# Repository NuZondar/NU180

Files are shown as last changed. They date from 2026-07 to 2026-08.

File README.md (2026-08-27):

# NU180
A reverse-engineered replacement for the U180 hybrid in the Hewlett-Packard / Agilent / Keysight 3458A DVM. 

Briefly, the custom "U180" hybrid in the 3458A is infamously prone to excessive drifting or outright failure, but is absolutely unavailable. NU180 is a drop-in replacement for that hybrid. Still under development, its performance falls slightly short of an original U180, e.g. noise performance is ~20-30% higher than spec, but it thus provides at least 8 digits conversion (within 2x of 8.5 digits), which is infinitely better than a dead or dying machine! 

Some notes:

The new Version 1.1 files are denoted "v11" in their names. 

The layout requires 6 layers. Choose a thin stack-up - that is, thinner core layers - if available. 

Choose the best resistors you can find, especially for their TCR (temperature coefficient of resistance). In particular, the use of low TCR bulk-foil resistors for at least the 50k and most-critical 80k's are recommended for best temperature stability. 

The footprints for the critical 80k's allow choosing either large 2512 surface-mount resistors, or else through-hole resistors (same for the 50k). These are intended for builders who are using bulk-foil resistors (80k's only come in 2512 size). You can edit the files to delete the unused footprints or else leave them in place. Another option for the 50k and 80k resistors is to edit the files to substitute a small array of series or parallel resistors. There's room for up to 4 each, e.g. 4x 20k in series for the 80k's, etc. 

You also have the option of using voltage regulation on the flip-flop and inverter (recommended), or else using unregulated 5V, chosen via jumpers. The schematic shows parts suitable for 3.3V operation, but other parts may allow operation down to 2.5V. The lower-voltage regulation should help keep noise down. 

The 100k resistors to ground are optional and need not be included unless some problem is seen. 

Debugging: The 3458A is a very sensitive instrument that can be quite fussy about error codes. At least in earlier versions, builders have sometimes found that changing the value of the series resistors (the 100 Ohm ones) up or down, e.g. to 33 or 220 Ohms, can help. Usually, only the four switch control lines associated with the 80k resistors (S5, S7, S9, S11) might need tuning. Another hack that has sometimes helped is adding a small capacitor (5-10 pF) in parallel with the R140 resistor on the A3 board.

There is extensive discussion of this project in the metrology section of EEVblog. Many people contributed their knowledge and experience towards its success, including MiDi, DB4UCH, wanghar, Kleinstein and others. 

Good luck!

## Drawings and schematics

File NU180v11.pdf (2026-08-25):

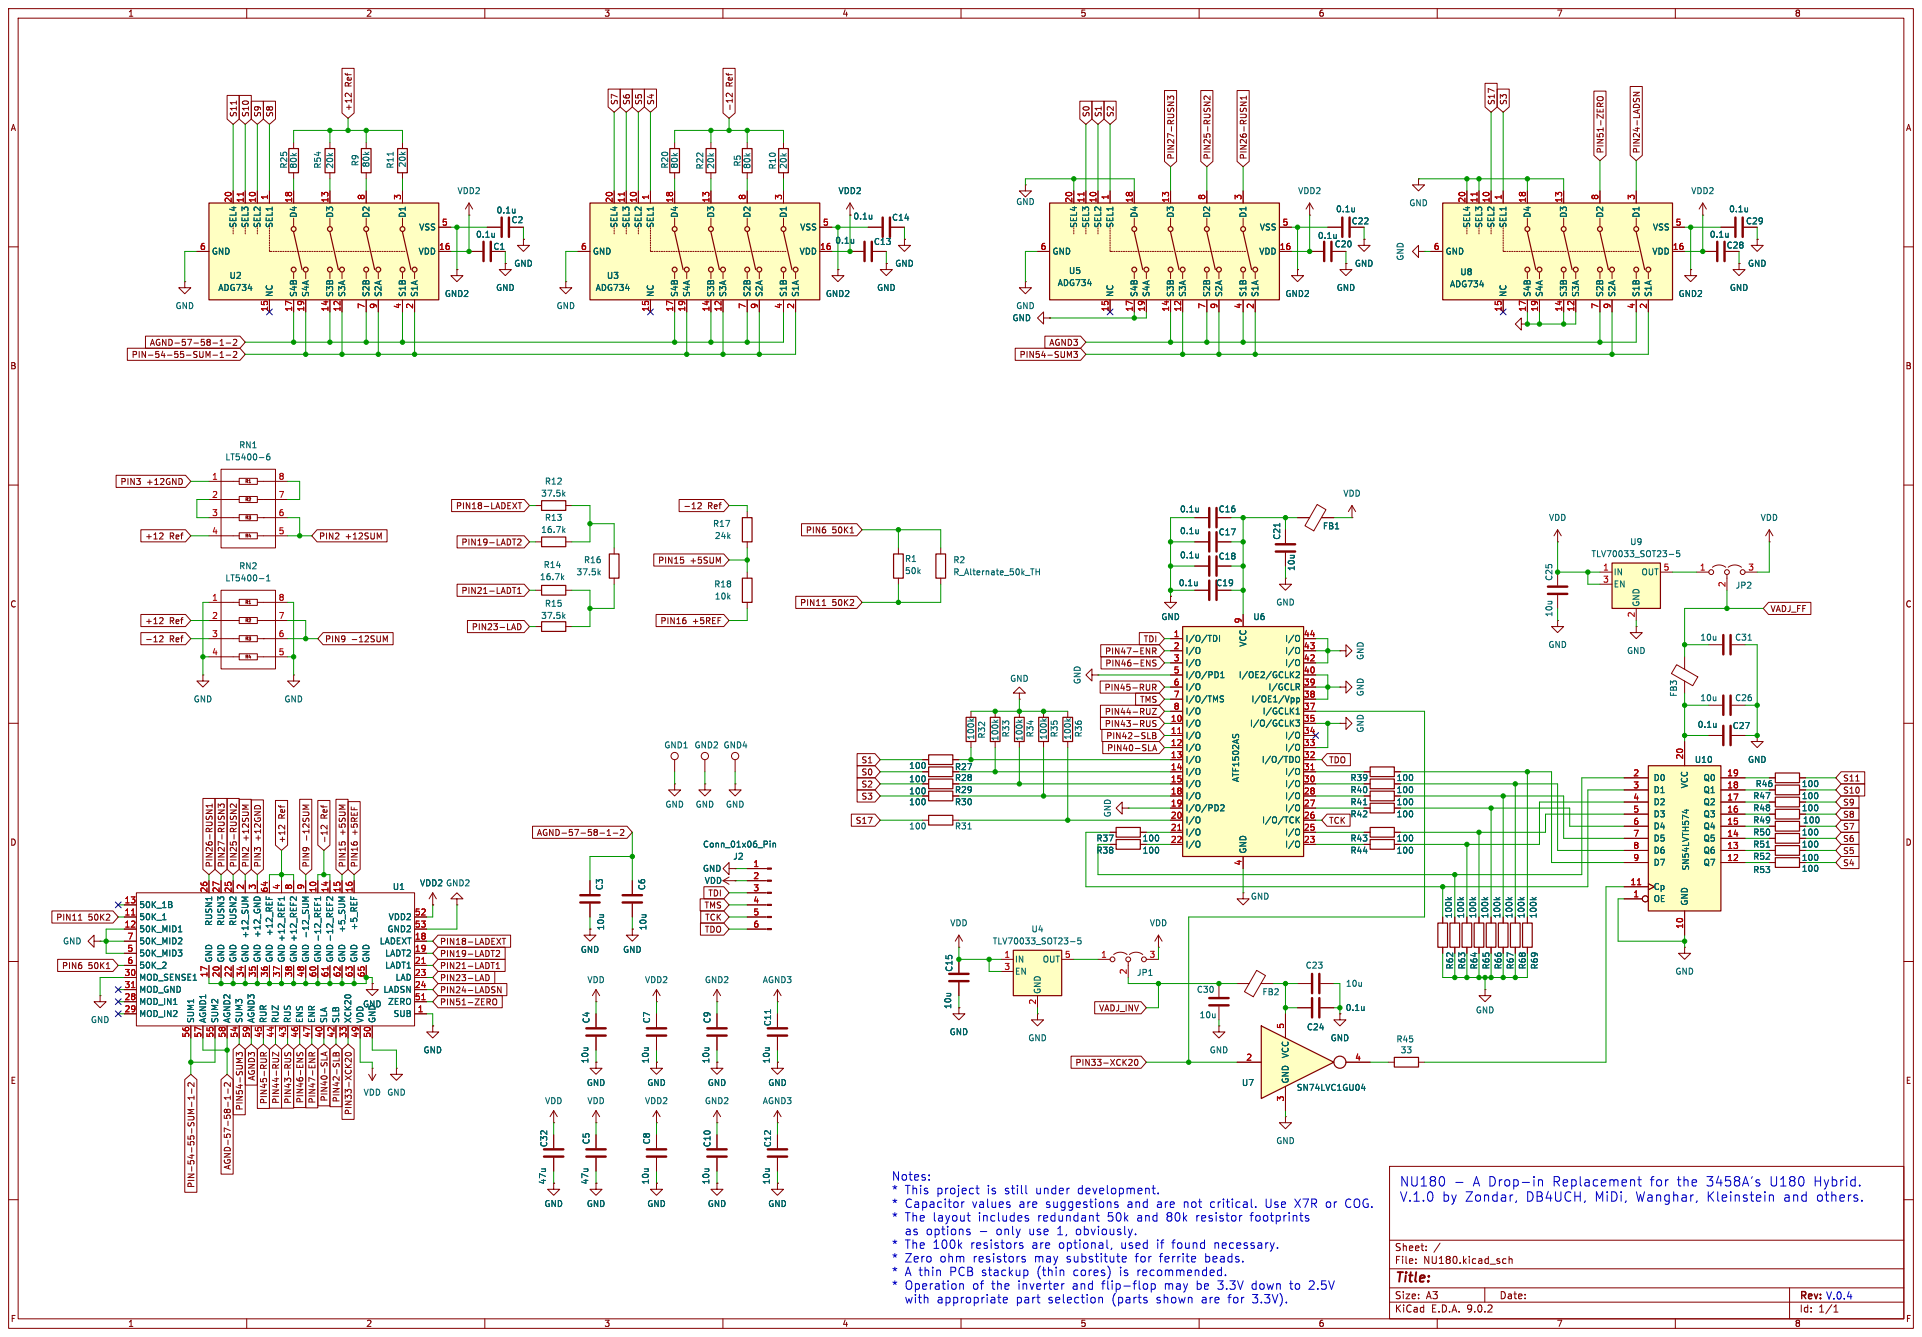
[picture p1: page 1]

2 OUT 5 U4 TLV70033_SOT23-5 GND GND2 GND GND C10 10u C6 10u GND

3 GND 35 RUR 45 +12_REF 64 GND 36 RUZ 44 +12_REF1

9 GND 48 ENR 47 -12_REF1 10 GND 60 SLA 40 -12_REF2 14 GND 61 SLB 42 +5_SUM 15 GND 62 XCK20 33 +5_REF 16 GND 63 VDD 49 GND 65 GND 50 VDD2 52 GND2 53

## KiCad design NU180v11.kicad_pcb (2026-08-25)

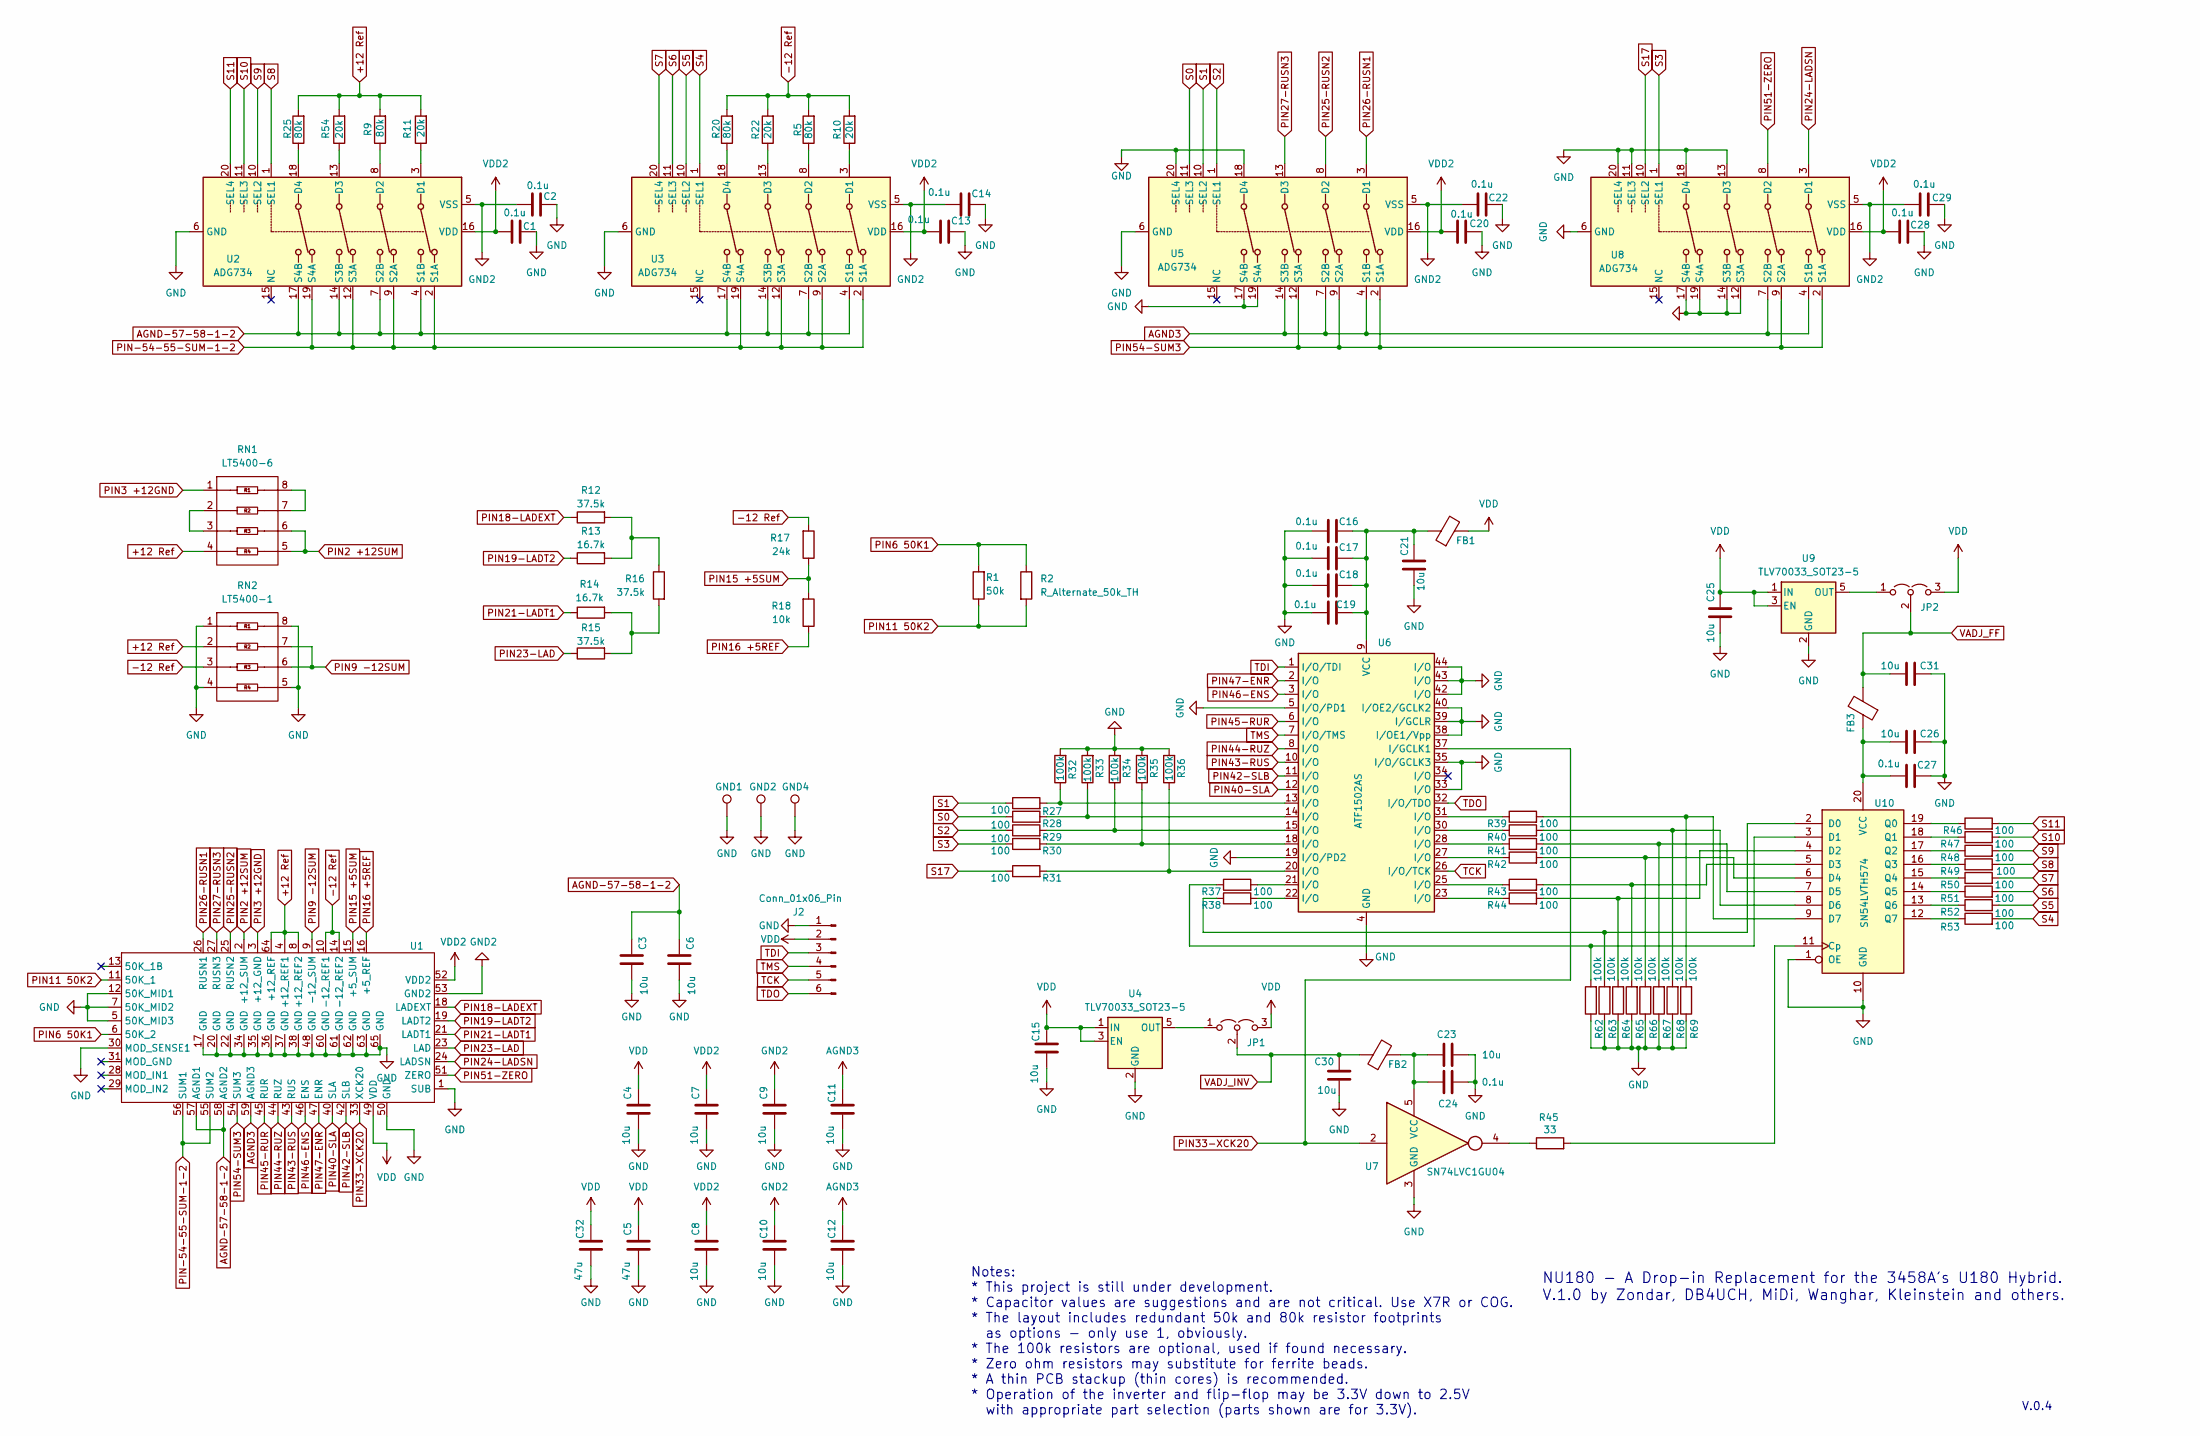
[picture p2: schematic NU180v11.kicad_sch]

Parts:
C1, C2, C13, C14, C16, C17, C18, C19, C20, C22, C24, C27, C28, C29: 0.1u; C_0603_1608Metric
C3, C4, C6, C7, C8, C9, C10, C11, C12, C15, C21, C23, C25, C26, C30, C31: 10u; C_0805_2012Metric_Pad1.18x1.45mm_HandSolder
C5, C32: 47u; C_1206_3216Metric
FB1, FB2, FB3: Ferrite Bead or Short; C_0603_1608Metric
GND1, GND2, GND4: TestPoint; PinHeader_1x01_P2.54mm_Vertical
J2: Conn_01x06_Pin; PinHeader_1x06_P2.54mm_Vertical
JP1, JP2: Jumper_3_Open; SolderJumper-3_P2.0mm_Open_TrianglePad1.0x1.5mm
R1: 50k; R_2010_5025Metric
R2: R_Alternate_50k_TH; R_Axial_DIN0204_L3.6mm_D1.6mm_P5.08mm_Horizontal
R5, R9, R20, R25: 80k; R_2512_6332Metric
R10, R11, R22, R54: 20k; R_1206_3216Metric
R12, R15, R16: 37.5k; R_0805_2012Metric
R13, R14: 16.7k; R_0805_2012Metric
R17: 24k; R_1206_3216Metric
R18: 10k; R_1206_3216Metric
R27, R28, R29, R30, R31, R37, R38, R39, R40, R41, R42, R43, R44, R46, R47, R48, R49, R50, R51, R52, R53: 100; R_0603_1608Metric
R32, R33, R34, R35, R36, R62, R63, R64, R65, R66, R67, R68, R69: 100k; R_0603_1608Metric
R45: 33; R_0603_1608Metric
RN1: LT5400-6; MSOP-8-1EP_3x3mm_P0.65mm_EP1.68x1.88mm
RN2: LT5400-1; MSOP-8-1EP_3x3mm_P0.65mm_EP1.68x1.88mm
U1: U180PINS
U2, U3, U5, U8: ADG734; TSSOP-20_4.4x6.5mm_P0.65mm
U4, U9: TLV70033_SOT23-5; SOT-23-5
U6: ATF1502AS; TQFP-44_10x10mm_P0.8mm
U7: SN74LVC1GU04; SOT-353_SC-70-5
U10: SN54LVTH574; TSSOP-20_4.4x6.5mm_P0.65mm

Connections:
+12 Ref: R9.2, R11.2, R25.2, R54.2, RN1.4, RN2.2, U1.4 (+12_REF1), U1.8 (+12_REF2), U1.64 (+12_REF)
-12 Ref: R5.2, R10.2, R17.2, R20.2, R22.2, RN2.3, U1.10 (-12_REF1), U1.14 (-12_REF2)
AGND3: C11.2, C12.2, U1.59 (AGND3), U5.4 (S1B), U5.7 (S2B), U5.14 (S3B), U8.4 (S1B), U8.7 (S2B)
AGND-57-58-1-2: C3.2, C6.2, U1.57 (AGND1), U1.58 (AGND2), U2.4 (S1B), U2.7 (S2B), U2.14 (S3B), U2.17 (S4B), U3.4 (S1B), U3.7 (S2B), U3.14 (S3B), U3.17 (S4B)
GND: C1.2, C2.2, C3.1, C4.1, C5.1, C6.1, C7.1, C8.1, C9.1, C10.1, C11.1, C12.1, C13.2, C14.2, C15.1, C16.1, C17.1, C18.1, C19.1, C20.2, C21.1, C22.2, C23.2, C24.2, C25.1, C26.2, C27.2, C28.2, C29.2, C30.1, C31.2, C32.1, GND1.1, GND2.1, GND4.1, J2.1, R32.2, R33.2, R34.2, R35.2, R36.2, R62.1, R63.1, R64.1, R65.1, R66.1, R67.1, R68.1, R69.1, RN2.1, RN2.4, RN2.5, RN2.8, U1.1 (SUB), U1.5 (50K_MID3), U1.7 (50K_MID2), U1.12 (50K_MID1), U1.17 (GND), U1.20 (GND), U1.22 (GND), U1.30 (MOD_SENSE1), U1.34 (GND), U1.35 (GND), U1.36 (GND), U1.37 (GND), U1.38 (GND), U1.48 (GND), U1.50 (GND), U1.60 (GND), U1.61 (GND), U1.62 (GND), U1.63 (GND), U1.65 (GND), U2.6 (GND), U3.6 (GND), U4.2 (GND), U5.6 (GND), U5.17 (S4B), U5.18 (D4), U5.19 (S4A), U5.20 (SEL4), U6.4 (GND), U6.5 (I/O/PD1), U6.16 (GND), U6.19 (I/O/PD2), U6.24 (GND), U6.33 (I/O), U6.35 (I/O/GCLK3), U6.36 (GND), U6.38 (I/OE1/Vpp), U6.39 (I/GCLR), U6.40 (I/OE2/GCLK2), U6.42 (I/O), U6.43 (I/O), U6.44 (I/O), U7.3 (GND), U8.6 (GND), U8.11 (SEL3), U8.12 (S3A), U8.13 (D3), U8.14 (S3B), U8.17 (S4B), U8.18 (D4), U8.19 (S4A), U8.20 (SEL4), U9.2 (GND), U10.1 (OE), U10.10 (GND); also elsewhere on the board
GND2: C2.1, C9.2, C10.2, C14.1, C22.1, C29.1, U1.53 (GND2), U2.5 (VSS), U3.5 (VSS), U5.5 (VSS), U8.5 (VSS)
unnamed: C16.2, C17.2, C18.2, C19.2, C21.2, FB1.1, U6.9 (VCC), U6.17 (VCC), U6.29 (VCC), U6.41 (VCC)
unnamed: JP1.1 (A), U4.5 (OUT)
unnamed: JP2.1 (A), U9.5 (OUT)
unnamed: R12.2, R13.2, R16.1
unnamed: R14.2, R15.2, R16.2
unnamed: R27.2, R32.1, U6.13 (I/O)
unnamed: R28.2, R33.1, U6.14 (I/O)
unnamed: R29.2, R34.1, U6.15 (I/O)
unnamed: R30.2, R35.1, U6.18 (I/O)
unnamed: R31.2, R36.1, U6.20 (I/O)
unnamed: R37.2, U6.21 (I/O)
unnamed: R38.2, U6.22 (I/O)
unnamed: R39.1, U6.31 (I/O)
unnamed: R40.1, U6.30 (I/O)
unnamed: R41.1, U6.28 (I/O)
unnamed: R42.1, U6.27 (I/O)
unnamed: R43.1, U6.25 (I/O)
unnamed: R44.1, U6.23 (I/O)
unnamed: R45.1, U7.4
unnamed: RN1.2, RN1.3
unnamed: RN1.7, RN1.8
unnamed: R11.1, U2.3 (D1)
unnamed: R9.1, U2.8 (D2)
unnamed: R54.1, U2.13 (D3)
unnamed: R25.1, U2.18 (D4)
unnamed: R10.1, U3.3 (D1)
unnamed: R5.1, U3.8 (D2)
unnamed: R22.1, U3.13 (D3)
unnamed: R20.1, U3.18 (D4)
unnamed: C23.1, C24.1, FB2.2, U7.5 (VCC)
unnamed: R45.2, U10.11 (Cp)
unnamed: R38.1, R63.2, U10.2 (D0)
unnamed: R37.1, R62.2, U10.3 (D1)
unnamed: R44.2, R64.2, U10.4 (D2)
unnamed: R43.2, R65.2, U10.5 (D3)
unnamed: R42.2, R66.2, U10.6 (D4)
unnamed: R41.2, R67.2, U10.7 (D5)
unnamed: R40.2, R68.2, U10.8 (D6)
unnamed: R39.2, R69.2, U10.9 (D7)
unnamed: R46.1, U10.19 (Q0)
unnamed: R47.1, U10.18 (Q1)
unnamed: R48.1, U10.17 (Q2)
unnamed: R49.1, U10.16 (Q3)
unnamed: R50.1, U10.15 (Q4)
unnamed: R51.1, U10.14 (Q5)
unnamed: R52.1, U10.13 (Q6)
unnamed: R53.1, U10.12 (Q7)
unnamed: C26.1, C27.1, FB3.1, U10.20 (VCC)
PIN2 +12SUM: RN1.5, RN1.6, U1.2 (+12_SUM)
PIN3 +12GND: RN1.1, U1.3 (+12_GND)
PIN6 50K1: R1.2, R2.1, U1.6 (50K_2)
PIN9 -12SUM: RN2.6, RN2.7, U1.9 (-12_SUM)
PIN11 50K2: R1.1, R2.2, U1.11 (50K_1)
PIN15 +5SUM: R17.1, R18.2, U1.15 (+5_SUM)
PIN16 +5REF: R18.1, U1.16 (+5_REF)
PIN18-LADEXT: R12.1, U1.18 (LADEXT)
PIN19-LADT2: R13.1, U1.19 (LADT2)
PIN21-LADT1: R14.1, U1.21 (LADT1)
PIN23-LAD: R15.1, U1.23 (LAD)
PIN24-LADSN: U1.24 (LADSN), U8.3 (D1)
PIN25-RUSN2: U1.25 (RUSN2), U5.8 (D2)
PIN26-RUSN1: U1.26 (RUSN1), U5.3 (D1)
PIN27-RUSN3: U1.27 (RUSN3), U5.13 (D3)
PIN33-XCK20: U1.33 (XCK20), U6.37 (I/GCLK1), U7.2
PIN40-SLA: U1.40 (SLA), U6.12 (I/O)
PIN42-SLB: U1.42 (SLB), U6.11 (I/O)
PIN43-RUS: U1.43 (RUS), U6.10 (I/O)
PIN44-RUZ: U1.44 (RUZ), U6.8 (I/O)
PIN45-RUR: U1.45 (RUR), U6.6 (I/O)
PIN46-ENS: U1.46 (ENS), U6.3 (I/O)
PIN47-ENR: U1.47 (ENR), U6.2 (I/O)
PIN51-ZERO: U1.51 (ZERO), U8.8 (D2)
PIN54-SUM3: U1.54 (SUM3), U5.2 (S1A), U5.9 (S2A), U5.12 (S3A), U8.2 (S1A), U8.9 (S2A)
PIN-54-55-SUM-1-2: U1.55 (SUM2), U1.56 (SUM1), U2.2 (S1A), U2.9 (S2A), U2.12 (S3A), U2.19 (S4A), U3.2 (S1A), U3.9 (S2A), U3.12 (S3A), U3.19 (S4A)
S0: R28.1, U5.11 (SEL3)
S1: R27.1, U5.10 (SEL2)
S2: R29.1, U5.1 (SEL1)
S3: R30.1, U8.1 (SEL1)
S4: R53.2, U3.1 (SEL1)
S5: R52.2, U3.10 (SEL2)
S6: R51.2, U3.11 (SEL3)
S7: R50.2, U3.20 (SEL4)
S8: R49.2, U2.1 (SEL1)
S9: R48.2, U2.10 (SEL2)
S10: R47.2, U2.11 (SEL3)
S11: R46.2, U2.20 (SEL4)
S17: R31.1, U8.10 (SEL2)
TCK: J2.5, U6.26 (I/O/TCK)
TDI: J2.3, U6.1 (I/O/TDI)
TDO: J2.6, U6.32 (I/O/TDO)
TMS: J2.4, U6.7 (I/O/TMS)
VADJ_FF: C31.1, FB3.2, JP2.2 (C)
VADJ_INV: C30.2, FB2.1, JP1.2 (C)
VDD: C4.2, C5.2, C15.2, C25.2, C32.2, FB1.2, J2.2, JP1.3 (B), JP2.3 (B), U1.49 (VDD), U4.1 (IN), U4.3 (EN), U9.1 (IN), U9.3 (EN)
VDD2: C1.1, C7.2, C8.2, C13.1, C20.1, C28.1, U1.52 (VDD2), U2.16 (VDD), U3.16 (VDD), U5.16 (VDD), U8.16 (VDD)

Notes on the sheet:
V.0.4
Notes: * This project is still under development. * Capacitor values are suggestions and are not critical. Use X7R or COG. * The layout includes redundant 50k and 80k resistor footprints as options - only use 1, obviously. * The 100k resistors are optional, used if found necessary. * Zero ohm resis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
NU180 - A Drop-in Replacement for the 3458A's U180 Hybrid. V.1.0 by Zondar, DB4UCH, MiDi, Wanghar, Kleinstein and others.

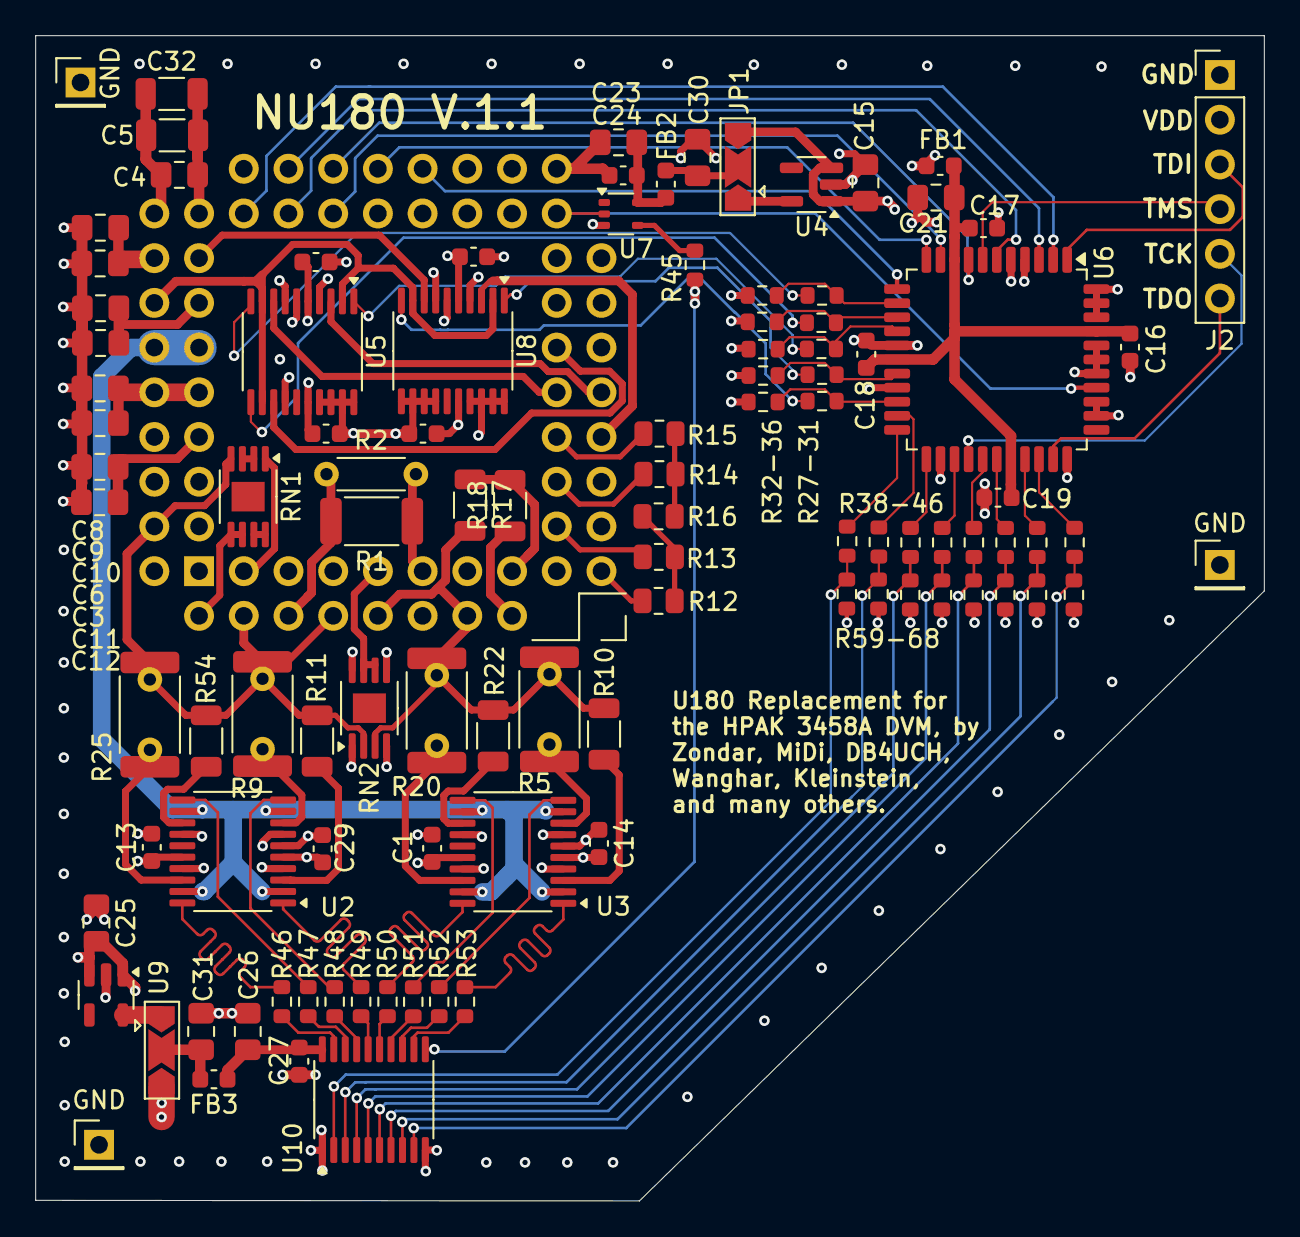
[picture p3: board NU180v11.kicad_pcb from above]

Board: 6 copper layers, 69.8 x 66.2 mm, 105 parts (0 on the bottom side), 101 nets.

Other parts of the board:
GND: TestPoint; PinHeader_1x01_P2.54mm_Vertical
GND#2: TestPoint; PinHeader_1x01_P2.54mm_Vertical

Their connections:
GND: GND.1, GND#2.1; also elsewhere on the board
